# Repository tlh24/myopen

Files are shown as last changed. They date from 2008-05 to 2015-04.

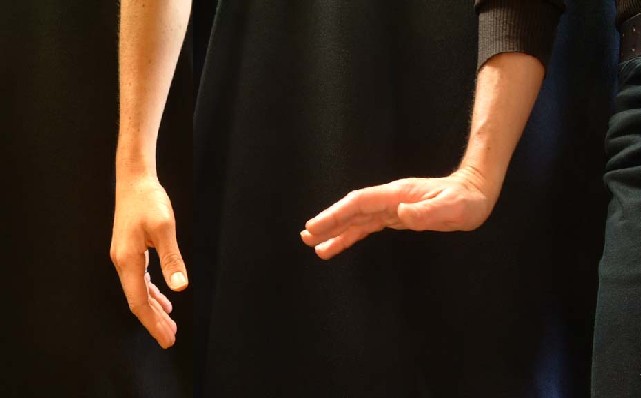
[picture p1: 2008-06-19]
MiniVIE/+PatternRecognition/Images/wrist extension.jpg

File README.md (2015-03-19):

# myopen
The Myopen project has expanded in include a number of separate modules: EMG hardware 9wired and wireless), EMG software, wireless neural recording hardware, wireless control software, and wired neural recording software.  Everything is released under GPL v3. Below is the old introduction. 

----

OPP is seeking to encourage experimentation with myoelectric control in order to inspire more rapid development of mechatronic prostheses for amputees. Because of the extremely small market size for upper extremity prosthetics, we think that one way to encourage this activity is to develop toys or user customizable devices that are capable of myoelectric signal processing. With wider access and experimentation with the technology, perhaps we could see interesting developments beyond the traditional venues of corporate R&D and educational institution research.

Along with a couple of collaborators (and we'd love to have more), we are exploring the development of an extremely flexible open hardware module that could be used with the Buglabs device, the LEGO NXT platform, and as a USB device that could be used with the OLPC (laptop.org), and traditional linux and windows computers. The components of the device would be modular, so we could populate them as needed, and use the same design for a variety of applications. The USB interface could also be used for connecting to game consoles, such as the Xbox360 and Playstation 3; the I2C bus may be useful for connecting to the Nintendo Wii via the Nunchuck input.

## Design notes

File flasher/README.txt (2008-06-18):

You need to have libparapin installed to make this work. 
http://parapin.sourceforge.net/
connections for making a cable: see flash.c
note: need a 33pf capacitor between clock signal and ground 
close to flash ram for proper timing.

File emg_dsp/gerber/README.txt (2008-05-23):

Project: emg_dsp, http://code.google.com/p/myopen/

Layer Stack: 
1 - Component, Cmp, top of board.  	emg_dsp-Cmp.pho
2 - L2, inner layer, ground. 					emg_dsp-L2.pho
3 - L3, inner layer, power/routing. 		""
4 - L4, inner layer, power/routing. 		""
5 - L5, inner layer, power. 					""
6 - Copper, Cop, bottom of board.   	emg_dsp-Cop.pho

Note: all layers are viewed from the TOP of the board. See layer texts on the right of the board
outside board outline. 

* PCB to be finished to 0.065" +- 0.005" thickness, unless otherwise required.  
* PCB to be constructed of FR4, high temperature option not required. 
* Rectangular routing outline in emg_dsp-Drawings.pho
* Minimum trace/space 0.005" 
* Minimim via drill 0.006"
* Drill file: emg_dsp.drl, summary in emg_dsp-drl.pdf
* Surface finish to be solder mask over bare copper (SMBOC), green, (in *Mask_ files), both sides. 
	with 150 micro inches Nickel (Ni)
	followed by 3-8 micro inches immersion gold. 
* Silkcreen (*SilkS_ files) to be white or yellow, both sides.
* Tear dropping alowed where permissible. 
* PCB to be manufactured in accordance with IPC-6011 and IPC-6012 class 2. 

Timothy Hanson
sideskate@gmail.com
919-475-4340 (cell)
919-668-1235 (office)

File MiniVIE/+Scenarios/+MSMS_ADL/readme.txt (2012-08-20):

% 6/18/2012

PPT files are located at: 
C:\MSMS\Sample Models\WRAMC_Model\Data\ADL

From XML files, .asf and .msm files are generated in:
C:\MSMS\Sample Models\WRAMC_Model\Data

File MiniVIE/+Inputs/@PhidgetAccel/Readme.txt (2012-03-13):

Matlab with Phidgets
April 18, 2008

Matlab gets access to the Phidgets via the Phidget21 C library.

In Matlab, we use .m files as 'code' files to hold the script to access a phidget.

To set things up all you need to do is change the working directory of Matlab to
wherever the examples are and then run the example by typing the filename in the
command window.

So servo.m which moves a servo is run by typing 'servo'

The code editor opens automatically when you double click a .m file 

Details about coding for matlab:

To open a system library: 

	loadlibrary phidget21 phidget21Matlab.h;

where phidget21Matlab.h is the header file located in the local directory and plib is a
handle to refer to the library from now on.

Note that phidget21Matlab.h is not the same as phidget21.h and has special modifications to
work properly with Matlab.

here we create a generic pointer which functions as a CPhidgetServoHandle 
(which is just a typedef of long anyways) and then use calllib to call the create function
from the library for initializing the ptr:

	ptr = libpointer('int32Ptr',0);
	open = calllib('plib', 'CPhidgetServo_create', ptr);

This gets the handle from the Phidget ptr, which we need for basically all function
ie: the handle is what the ptr points to:

	handle = get(ptr, 'Value');

We then need to open the servo motor and wait until it's status indicated an attach.

Here we use the handle and also an int32 pointer to call getSerialNumber, since
we need to pass a pointer to int for the serial number:

    serial = libpointer('int32Ptr',0);
    calllib('plib', 'CPhidget_getSerialNumber', handle, serial);

We also use a timer to time the setmotorposition's but that's a matlab thing, not really important.

Note that there is no concept of funtion pointers in matlab, so we can't use events at all.
This means that we have to poll for the data. This also means that we can't use the attach event.
Since we have to use some sort of method to wait for attachment, we can use the CPhidget_waitForAttachment
method to wait for the attachment. This method takes in a handle and a timeout, with a time of 0 meaning
infinite and it won't return until the phidget is attached or the timeout expires, so you need to check
the return value - see the examples for this.

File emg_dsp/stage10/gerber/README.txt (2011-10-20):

Project: stage10, http://code.google.com/p/myopen/

Layer Stack: 
1 - Front, top of board.  				stage10-Front.gtl
2 - L1, inner layer, ground. 			stage10-Inner2.gbr
3 - L2, inner layer, power/routing. 		stage10-Inner3.gbr
4 - L3, inner layer, power/routing. 		stage10-Inner4.gbr
5 - L4, inner layer, ground. 			stage10-Inner5.gbr
6 - Back, bottom of board.   			stage10-Back.gbl

Note: all layers are viewed from the TOP of the board. 

* PCB to be finished to 0.063" +-0.006" thickness (1.6mm) 
* PCB to be manufactured in accordance with IPC-6011 and IPC-6012 class 2. 
* PCB to be constructed of FR4, high temperature option required, Tg >= 170C
* Routing outline in stage10-Drawings.gbr
	Board external dimensions: 3.05"(y) by 4.35"(x) exactly. 
* Minimum trace/space 0.005" / 0.005"
* Minimim via drill 0.008"
* Drill file: stage10.drl
* All holes to be plated through.
* Surface finish to be solder mask over bare copper (SMBOC), blue, 
	in stage10-Mask_Front.gts and stage10-Mask_Back.gbs, both sides. 
	with 150 micro inches Nickel (Ni)
	followed by immersion gold. 
* Solder mask may be enlarged as needed. 
* Silkcreen in stage10-SilkS_Front.gto , stage10-SilkS_Back.gbo  
	to be white, both sides of board.

Timothy Hanson
sideskate@gmail.com
919-475-4340 (cell)
919-668-1235 (office)

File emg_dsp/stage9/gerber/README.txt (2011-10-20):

Project: stage9, http://code.google.com/p/myopen/

Layer Stack: 
1 - Front, top of board.  				stage9-Front.gtl
2 - L1, inner layer, ground. 			stage9-Inner2.gbr
3 - L2, inner layer, power/routing. 		stage9-Inner3.gbr
4 - L3, inner layer, power/routing. 		stage9-Inner4.gbr
5 - L4, inner layer, ground. 			stage9-Inner5.gbr
6 - Back, bottom of board.   			stage9-Back.gbl

Note: all layers are viewed from the TOP of the board. 

* PCB to be finished to 0.027" +0.005" -0.002" thickness (0.68mm) 
* PCB to be manufactured in accordance with IPC-6011 and IPC-6012 class 2. 
* PCB to be constructed of FR4, high temperature option required, Tg >= 170C
* Routing outline in stage9-Drawings.gbr
	Board external dimensions: 2.4"(y) by 1.9"(x) exactly. 
	Some silkscreen will be cut off board; this is OK. 
	Tight copper/routing clearance at bottom is per design. 
* Minimum trace/space 0.005" / 0.005"
* Minimim via drill 0.006"
* Drill file: stage9.drl
* All holes to be plated through.
* Surface finish to be solder mask over bare copper (SMBOC), blue, 
	in stage9-Mask_Front.gts and stage9-Mask_Back.gbs, both sides. 
	with 150 micro inches Nickel (Ni)
	followed by immersion gold. 
* Solder mask may be enlarged as needed. 
* Silkcreen in stage9-SilkS_Front.gto , stage9-SilkS_Back.gbo  
	to be white, both sides of board.

Timothy Hanson
sideskate@gmail.com
919-475-4340 (cell)
919-668-1235 (office)

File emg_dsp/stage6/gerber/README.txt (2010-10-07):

Project: stage6, http://code.google.com/p/myopen/

Layer Stack: 
1 - Front, top of board.  				stage6-Front.gtl
2 - L1, inner layer, ground. 			stage6-Inner2.gbr
3 - L2, inner layer, power/routing. 		stage6-Inner3.gbr
4 - L3, inner layer, power/routing. 		stage6-Inner4.gbr
5 - L4, inner layer, ground. 			stage6-Inner5.gbr
6 - Back, bottom of board.   			stage6-Back.gbl

Note: all layers are viewed from the TOP of the board. 

* PCB to be finished to 0.063" +- 0.006" thickness (1.6mm) 
* PCB to be manufactured in accordance with IPC-6011 and IPC-6012 class 2. 
* PCB to be constructed of FR4, high temperature option required, Tg >= 170C
* Routing outline in stage6-Drawings.gbr
* Minimum trace/space 0.005" / 0.005"
* Minimim via drill 0.006"
* Drill file: stage6.drl
* All holes to be plated through.
* Surface finish to be solder mask over bare copper (SMBOC), blue, 
	in stage6-Mask_Front.gts and stage6-Mask_Back.gbs, both sides. 
	with 150 micro inches Nickel (Ni)
	followed by immersion gold. 
* Solder mask may be enlarged as needed. 
* Silkcreen in stage6-SilkS_Front.gto , stage6-SilkS_Back.gbo  
	to be white, both sides of board.

Timothy Hanson
sideskate@gmail.com
919-475-4340 (cell)
919-668-1235 (office)

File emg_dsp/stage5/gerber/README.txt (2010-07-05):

Project: stage5, http://code.google.com/p/myopen/

Layer Stack: 
1 - Front, top of board.  				stage5-Front.gtl
2 - L1, inner layer, ground. 			stage5-Inner2.gbr
3 - L2, inner layer, power/routing. 		stage5-Inner3.gbr
4 - L3, inner layer, power/routing. 		stage5-Inner4.gbr
5 - L4, inner layer, ground. 			stage5-Inner5.gbr
6 - Back, bottom of board.   			stage5-Back.gbl

Note: all layers are viewed from the TOP of the board. 

* PCB to be finished to 0.047" +- 0.006" thickness (1.2mm) 
* PCB to be manufactured in accordance with IPC-6011 and IPC-6012 class 2. 
* PCB to be constructed of FR4, high temperature option required, Tg >= 170C
* Routing outline in stage5-Drawings.gbr
* Minimum trace/space 0.005" / 0.0045"
* Minimim via drill 0.008"
* Drill file: stage5.drl
* All holes to be plated through.
* Surface finish to be solder mask over bare copper (SMBOC), blue, 
	in stage5-Mask_Front.gts and stage5-Mask_Back.gbs, both sides. 
	with 150 micro inches Nickel (Ni)
	followed by immersion gold. 
* Solder mask may be enlarged as needed. 
* Silkcreen (stage5-SilkS_Front.gto , stage5-SilkS_Back.gbo ) to be white or yellow, only top of board

Timothy Hanson
sideskate@gmail.com
919-475-4340 (cell)
919-668-1235 (office)

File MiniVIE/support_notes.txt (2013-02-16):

Support Notes
--------------

Tested with Matlab 2010b on WindowsXPSP3 32-bit
Tested with Matlab 2010b+ on Windows7 64-bit (all execpt DAQ toolbox)

Requirements: 

For use of the DiscriminantAnalysis SignalAnalysis Classifier modules
Statistics Toolbox

For use of the DaqHwDevice input object
Data Acquisition Toolbox.  See http://www.mathworks.com/products/daq/requirements.html

Data acquisition toolbox notes:
* For external DAQ devices, these typically require third party driver software.  

* Measurement Computing products need the InstaCal driver software installed.  
  Channel modes (e.g. differential versus single ended) should be configured with that tool

* National Instruments board require the nidaqMX driver suite, available from the NI website
  The complete install package is ~1.5GB, however you can alternatively download and install
  the nidaqmx_core library which is only ~150 MB

* Important: Please follow the instructions for registering the install DAQ device with the 
  MATLAB environment.  This typically takes the form:
  >> daqregister('nidaq')  % RUN AFTER LAUNCHING MATLAB IN ADMINISTRATOR MODE

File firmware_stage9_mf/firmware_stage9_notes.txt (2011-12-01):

December 1 2011
	Thoughts: really should put the LMS *after* filtering -- it just serves to 
	get rid of the 60Hz, which the filters can deal with effectively already. 
	If it's after the IIR fitlers, it will 'concentrate' more on in-band common-mode
	noise.

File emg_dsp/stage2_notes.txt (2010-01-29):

stage2 notes: 
x array distance on the LMV1023 circuit: 0.247"
y array distance : 0.057

Feb 11 2009: changed input capacitors from 1uf to 0.47uf to have 
better rejection of ECG; updating the digikey order accordingly. 

March 10 2009 - 
NEED THERMAL RELIEF around all through holes; otherwise, cannot solder them! 
(at least, not with a soldering iron; may be able to reflow them)
NEED more space around the electrolytic cap -- or need a surface mount cap. 
	 I'm just going to leave it out for now. 
NEED to get the large-bumped package for electret amps: LMV1032UR
FOOTPRINT for SOD-523 and SOD-323 are incorrect; need to use SOD-523 for both 
	on board (3.3 and 5v zener protection).  
	http://www.diodes.com/zetex/_pdfs/3.0/pack/SOD523.pdf
	http://www.diodes.com/zetex/_pdfs/3.0/pack/SOD323.pdf
	323 is BIGGER than 523 (wha?)
FOOTPRINT of nRF24L01 too small - fixed. 
	the top pads were off by 0.25mm !  (1.5mm instead of 1.75mm - 
	changed to 1.85mm for better exposed die clearance)
FOOTPRINT of LFCSP-48 enhanced.  should be OK now, though - just no overhang. 
	set overhang to 0.2mm. 
VOLTAGE of the MAX3421E is 3.3V - it does not run at 2.85V!! DOH! 
	next time need a 3.3v LDO off the USB power for this chip!

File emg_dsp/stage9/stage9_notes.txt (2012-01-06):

Fixes to stage9: 
* Need to have a hole or somethingunder the 9-pin omnetics conmnectors: 
	connectros shear off easily
	Alternately, need a different connector system. 
* Bipolar transitor on the input to prevnt breaking in the case the battery polarity is wrong
* Lower voltage (0.85v) , lower clock rate w/ simpler firmware
* Use cuts not jumpers for the ground / reference configuration. 
** Slight ground currents should not matter, I hope. Need to think about this. 
* Realy should use the impedance measurement -- should be a very useful feature. 
* Also, an accelerometer or some other way of measuring state ... will have to transmit that
** can multiplex on one continuous channel.
* LFP would be nice too. Expand the analog filtering? 
* Might be nice to use something else to derive the MUX signals, and do block computation? 
	Have to think about this .. issue is that we are wasting clocks sometimes waiting for samples.
	Really need a much lower-power processor. 
* Add 2-4 channels microstim(?).  Must be careful about ground-loop: use a separate proc. 
	or a separate battery; have to think about this.

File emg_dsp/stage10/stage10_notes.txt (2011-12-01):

fixes to stage10: 
 * need to connect R118 to ground. This is the APD signal on the PoE chip.
 	(not absolutely needed for device function, but should be fixed.)
 * regulated output of PoE converter is 2.5v -- off by a factor of 2? 
 * Anode and cathode are reversed on the TLE431 (!)
 * Really need to have a switch on the PoE input -- so we can turn off the switching there.

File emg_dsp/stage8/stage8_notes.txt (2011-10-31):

Notes from debugging stage8
February 25 2011
* Most everything works properly on the board -- no hardware errors yet.
* Digikey shipped some incorrect resistors, which is annoying - they 
	have not done this before, to the best of my knowlege - 
	but a relatively easy fix. 
* The new solder paste - ZeroLead no-clean solder paste - 
	http://www.ameritronics.com
	works well, better than previous.  Unfortunately they don't ship with caps. 
* Issue: headstage seems to be transmitting data well (at least looking
	at the control signals).  RX fails about 50% of the time.
	only thing that has changed is the incoming data rate. 
	Hence, let's try writing data more slowly - at original rate.
		same issue.
		probably is something in the radio code.. 
	Perhaps it's a framing isue: SPI clock too slow, some bits get cut off?
		changed rate to 13.3Mhz - no change. 
		Strangely, we seem to get IRQs in the middle of where they should be.
		Notable is we've changed the cycle time from 2us to 1us
		natrually there will be issues.
		Added some extra pipeline stalls, nothing..
		Perhaps should try slowing down the sample clock for the same effect?
		Halved the sample rate -- did not fix problem. 
		Still unreliable packet transmission.
		Must be the radio control code.
		Try the C-version: seems broken! JTAG time.
	C version working.  SPI clock running at 10Mhz, as per asm version.
		primary difference seems to be that the packets are uploaded in bursts, 
		not continuously like the other. try change.
		continuous packet uploading does not break C version for radio controller.
		Let's compare..
		seems there's an extra clearfifo bizness... check if that makes it work.
		radio_clearfifos makes the return packet arrive more reliably, yes.
	Think the radio control routine is the same as the C version -- 
		have not checked with JTAG yet -- 
		but still does not work :-(
		aggregate data rate appears to be about the same
		data bus appears to be active at the right times..
		where are the extra / skewed packets coming from? 
		is this a data content issue? 
February 28 2011
		YES
		changing the data to 0xa5 for all samples fixed the error!  yay!
	Proc seems to be waiting too long for the RX packet. 
		usually the bridge can respond within 360us
		presently we're waiting 780us
		current serial RFS is 29 / was 19 -> equivalent wait of 511us
		Should wait 180 samples; 190 ought to be enough.
			(there are two calls to _get_asm in the loop of waitirq)
	Perhaps I've overestimated the outgoing bandwidth. 
		It takes 1.36ms to transmit 256 bytes (measured)
		It takes 360us for the bridge to turn around and get a response.
		Total is 1.72ms. 
		Frame time, with 7 samples per packet, 56 samples per frame is 1.792ms
		much too close, apparently! 
		setting waitirq to 172 allows the 'stage to work.. not exactly sure why though.
		anything below 160 misses out on TX sent IRQs.
	Really need to fix the data bug - simplest, and best, way is to add AGC. 
		working on AGC: IS (integer signed) mode is
		ESSENTIAL
		when transferring accumulator to register.
March 1 2011
	Got AGC working properly.. finally. 
		Turned out that i hadn't though of the magnitude of the components properly.
	Next, most important issue: make radio transmission reliable. 
		If we transmit 0xa5 for all bytes, all packets seem to get through.
		If we transmit 0xcc, same.
		0xc0, same.
		0x80, same.
		0x00?  same!!
		0xff?  fail!! aha.  I guess.
		0xfe? works..?
		0x01, works.
		XOR data with 0xa5 fails.
		AND data with 0x7f fails.
		AND data with 0xbf fails.
		AND data with 0xdf fails.
		AND data with 0xef fails.
		AND data with 0xf7 fails.
		AND data with 0xfb works.
		AND data with 0xfd works.
		AND data with 0xfe works.
		
		Slowing down the SPORT to half the speed - hence giving more time between 
		SPI transfers - does not fix the issue.
		whattt is it? perhaps contention - something else (nordic?)
		is trying to drive bus?
		Doesn't look that way - the busses are separate. 
		Which byte is it?  can possibly send 0xaa as the first byte, technically only need
		31 bytes payload.
March 2 2011
	(Continuing above)
		Tried sending 0xa8 as the first byte .. reception is still noisy. 
		What if we change the radio channel? 
		Why did this error not appear before?  Is it hardware-dependent?
	trying stage5. 
		it RXes every other packet,  more or less.
		but program does not fit hardware well... hmm.
	trying different radio channel (0) -- no change. 
		same issue. dropped packets. 
	trying to AND data with 0xfe - 8 bit TX to 7 bit - make difference?
		yea.  that works.  WHYYYY?
	Ok, I understand why - the bridge is getting confused by the new packet setup, 
		and is spontanteously going into RX mode during a frame, thereby missing 
		vital packets. 
		What we need to do is re-write the bridge code to accomidate the higher b/w
		and possibly to extend the frame to 16 packets. 
	Trying the processor at 400Mhz -
		looks like the MAD does not work, or does not complete in time, at this frequency. 
		really should increase the core voltage. 
		At a core voltage of 1.0v (was 0.85v), the processor seems to run normally. 
		current is 100ma. (about)
		Stops working just at 0.85v.
		That said, looks like @ 400Mhz we have plenty of time for adaptive noise
		cancellation, if it's decided that will help! 
		(at what place in the pathway should we do this - befroe AGC I guess?)
April 8 2011
	Current consumption: 
	60mA, 4.12v, everything enabled, one LED on 5ma 2.85v -> 3.5ma@ src
		should be 56.5ma w/o LED. 
	47.5ma, 4.10v, two headstages connected, one LED -> 44.0ma @ src
	41.8ma, 4.10v, one headstage connected, one LED -> 38.3ma @ src. 
	----
	each headstage consumes about 6ma from the source. 
	The intans are listed at about 4.1ma each (supplied directly from bat, not switched)
	The ADC is listed at 2mw -> 0.75mA, also supplied from the bat, 
	so we have about 1.2ma unaccounted for --
	probably attributable to computation? 
	or the intans use more current than expected?
	Well, anyway. let's say 60ma, want the thing to run for 24 hours. 
	That's 1440maH.  can get that in a cell phone battery .. easy. yay! 
	do i want to record more than 128 channels? nah. 
	----
	Other things to do: 
	* audio out working on base station. constant rate sample consumption? 
	 variable rate? hm. (fixed)
	* decorrelator in the spare cycles?  (done)
	* fractional gain (done)
	* flat response has inappropraite gain?  (fixed)
	* sample different parts of the signal chain. (done)
	* longer waveform drawing -- should go to the end of the screen in zoom = 0.2
		(done)
	* be able to turn AGC off. 
	* fix the draw bug on neuro-nico. seems to be pre-GPU, since if you switch 
		the indicies of the VBOs, the yellow is then drawn correctly.
		methinks its a 64-bit issue. which is indeed an issue.
	----
April 9 2011
	Tested radio + triple diversity RX -> works very well. 
	Can position the transmitter by the window & not have too too many dropped packets.
	add another filter option? 
April 14 2011
	Implemented 3 versions of LMS: 
	* simple, direct 7 tap filter, error computed via shift >>>
	* pseudo-LMS style, error saturated to +- 1, signal saturated to +- 1
	* summing pseudo-LMS style, sum 3 samples, 4 weights, sum saturated to +- 1, 
		error saturated to +- 1.
April 18 2011
	* Noted that audio output seems to contain pops and clicks; worried that 
	this may be a result of 
	(1) processor operating at a too high clock rate -> errors in math
	(2) errors in transmit pipeline due to stalls. 
	To test
	(1) clocked proc slower. 288Mhz, 720kHz ADC. 
		No change in pops as recorded to disc.  
		the pops seem poisson - most likely the radio is at fault!
		Can we detect these as false spikes? 
	(2) clocked ADC slower. 800Khz -> more cycles to service radio.
		No change in pops as recorded to disc.
	Looking at the data, it is clear that sometimes the packets are *not*
	being sent out on the wire in order - some packets are dropped, but 
	the ones put in their place are not always those dropped. 
	It almost looks like they were hanging around from some old buffer. 
	And this appears poisson ..? Network noise?
	Must be a bug in the stage7 firmware.
	Observations: 
	* Never messes up channel assignment - when channels have two different
		sine wave amplitudes, the pops never exceed that amplitude.
	* Errors are concomitant, generally - the occurr on a per-packet basis
		The only time you only hear on one channel is when the error is less audible 
		on the other channel.
	* Error is alwas preceded by a dropped packet - less noticeable - and an 
		addition of an unkown packet. 
		Is this packet a reminant of an old transmission? 
		Will have to erase after write-out to see! 
	YES, if we clear the buffer to 0, all unkown packets are 0 packets. 
		must be that 'gotx' or 'go tx' is being triggered before the buffer is
		completely full (recall frame = 16 packets; UDP_PACKET_SIZE = 512 = 32*16)
		This implies that packets are being dropped, which is not surprising, 
		even though the radios are right next to eachother..?
		What about antenna diversity? Could be that another antenna RXed the packet.
		Really need to analyze antenna diversity & how the SW degrades. 
		The only reason I have packet transmission tied to RX packet is that 
		this seems like a good pause for servicing eth..
	okay. now the packets are properly dropped rather than having bogus data inserted. 
	Next: check antenna diversity.
		Antenna diversity is working!  any of the three antennas is capable of picking
		up signal. However, three together do not seem to reduce the error rate to zero. 
		perhaps it is exogenous noise? 
		or ethernet interupts? 
		Kinda hard to test the eth theory -- we need to listen to packets!
		Try disabling the audio out? 
			No difference.
			Maybe I should just sleep on it.
	Ok, try to fix the audio out, which is emmiting wobbly shit.
		putting it in only normal mode. lots of staticky noise, probably from having 
		only 16-bit samples. 
		bah, need an antialiasing filter here.
April 19 2011
	Testing headstage current: 
	(everything running, full LMS 320Mhz / 80Mhz / 1Mhz ADC)
	3.11V	75.1ma  (minimum voltage - below this signal is distorted - probably LDO drop-out)
	3.20	73.2
	3.30	71.6
	3.41	69.4
	3.56	67.3
	3.71	65.9
	3.83	64.6
	3.96	63.1
	4.07	62.0
	4.23	60.6
	4.38	59.3
	4.49	58.5
	4.57	57.9
	4.77	56.6
	5.04	55.0
	5.21	54.1
	5.34	53.5
	5.64	52.0
	5.80	50.9
	6.05	49.8
	6.19	49.2
	6.35	48.7
	Linear fit gives: static power consumption 153 mw (with LED!), 24.6mW/V slope
	(so about 25ma static draw, 50ma dynamic @ 3V)
	check: 4V / 150mw = 38.25 dynamic + 25 static = 62.85Ma; actual = 62.15.
	Capacity required with a mean Li-ion voltage of 3.56V - 24*67.3 = 1615maH
	probably want at least 2000maH, or better. 
	could reduce code complexity to reduce power .. but I hope all this stuff is useful.
May 25 2011
	Added template sorting to both headstage and client -- whew. 
	Have to clock the processor at 0.95V, 400Mhz now; 
		let's check the power consumpion.
	3.31	84.2ma	278mw
	3.50	80.5	281
	3.70	77.9	288.23
	Assuming average current consumption of 80ma (note - with LED), 
	one RediLast 2900 battery should power one headstage for 36 hours. 
		(if not more - see 
		http://lygte-info.dk/info/Batteries18650-2011%20UK.html 
		which shows 10.5Wh -> 37hours @ 282mw)
October 26 2011
	Jesus!  Where did the time go? 
	Still confused about the "headstage says match, we don't find" error. 
	Is it bit-error noise? 
	Have to make sure the aperture & template are being updated properly;
		I have a suspicion that the GUI is not always being updated, esp. after sorting (?)
		Seems to update after sorting, yes. 
	Ok, juice!

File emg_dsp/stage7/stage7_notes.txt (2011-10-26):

Hardware fixes: 
	* Need filtering on the testcon _CS signal too! 47pf fixes issue. 
	* MIC5365-2.5 supplying Votp for blackfin is not attached to Vdd. 
		fixed in schematic.
	* Labels on LEDs are incorrect. 
	** Be very careful about LED orientation in robot! 
	* Capacitors on audio out are mounted too close to the 1/8" jack body.
		can fix with sensible placement prior reflow.
		
Software: 
	March 25 2011 -- 
	one radio seems to work well; interaction of all 3 radios, 
		however, does not work. Looks like radio 0 tmies out at some point,
		holding it's CSN line low. 
		what would be doing this? 
		(as an aside, reverse directon seems not to work - 
			cannot modify headstage channel)
		trying to enable 2 radios.
		Ok, with two radios, looks like radio1 is not always after radio0,
			and that twice as much data is coming out of the bridge.
			(the 2 channel scope is a real liability here). 
			(I really need to get my logic analyzer)
	got three radios working .. seemingly. 
		getting about 10530 packets/second in the client. 
		for 128 channels, measured frame rate is 279.3 frames/sec, 
		which equates to 4468 packets/second.  Observed rate is 2.35 times larger - 
		clearly I need a better means of radio state control. 
		I think what's going on is that the program is desynchronized with 
		incoming radio packets: we are setting 'write' to 1 when
		one radio still has a packet in the fifo.  
		Therefore only set write to one when all radios are serviced? 
		woohoo looks like antenna diversity is working! yay.
		now need to check on the thresholding. 
	thresholding: why no work? 
		deal: need to test with *actual* signals, not just noise.
		behavior: changing the channel works. 
		setting the threshold makes the threshold crossings more realistic. 
			changing the threshold seems to not change threshold crossing density.
		changing the channel subsequently reverts threshold channel display.
		aright, that's fixed - pointer wrap issue.
		now the problem is that the display is fruitcaked. as in, caked in fruit.
		spikes are not aligned with threshold crossings. 
		breaking down the issue further, fixed the channel ordering problem; 
		now it seems that the order of thresold crossings in the spike display 
		is inverted per 32 channels. 
		that would be because that's the way it is in the schematic! 
	need to test by setting channels to oscillate (sinusoid)

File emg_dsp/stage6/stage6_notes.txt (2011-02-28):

Hardware Fixes: 
	* The LEDs are TOO bright!  decrease the current to a more reasonable 
	level.  Current LEDs Vf = 2.0V :: 26mA of current. 10ma better -> 
	need 130 ohm resistors.
	Total power dissipation of 16 LEDs: 1.3W..?
	* Vdd_OTP NEEDS to be tied to 2.5V for the proc to boot.
	I guess I'll need a regulator here.
	(I assume this is needed by the security code)
	* Need caps on nordic lines to quench ringing (47pf, SCK & MOSI)
	* R61 & friends were not grounded (on the schematic) oops!
		Can jumper to R12.
	* The labels on the external power supply are SWAPPED! 
		28 is 0.8V, 08 is 2.8V! (or more accurately, 2.65V, as measured)
	* On EMG section, input to OR gate must be RSCLK0, not TSCLK0. 
		TSCLK0 is only used to generate TFS0.
		Both clocks are output. 
	* switching regulator needs to be further away from EMG input section.

November 8 2010
	* Wrote a simplified .dxe - one that just toggles a few pins - 
	and the BF527 seems to run. Next: see if we can get the SPI interface running. 
	(this will show if the SPI pins are connected - the proc does not boot, 
	but this is likely because the flash originally ordered was a 2V part)
	* putting the SDRAM in self refresh works. 
	* setting the core clock at 600Mhz and the system clock at 125Mhz 
	seems to work as well. the toggle rate is 6.666Mhz now; was 1.5Mhz.
	(I'm sure glad JTAG works!!!)
	* looks like the SPI port is working! Not sure why it doesn't try to boot..
	* Next task: get the UART working. soo useful. done.
	* SDRAM: initalized.  works, checked!  yay!
	* Ethernet: need to have a milisecond counter running first, in an interrupt.
	* Ethernet: works.  DCHP and all!
November 9 2010
	* Next: get the radio working. Needs to be soldered there first! 
November 12 2010
	* okay, the bridge - at least in a debug build - seems to work. 
	The radio is very sensitive to timing / sequencing: notably, NRF_CE
	must be low while uploading the response (command) packet.  
	so be it.  
	* -O3 does not work, for whatever reason.  ??  just use -O or -O2.
	* if you put the headstage in oscillate mode, it still appears that there
	 are dropped packets. perhaps it is the client..?
	 the trace from UDP packets indicates that nothing is being dropped, 
	 and the o-scope similarly looks good. 
November 15 2010
	* I guess the next thing is to try out the new version of the headstage..
	does not seem to transmit packets reliably. electrical issue?
	tried hand-soldering all the pins again - from the outside, without removing
	the chip, and no difference. 
	perhaps in the future I should have protronics put both the RHA2116 and 
	nRF24L01+ on the board?  Seems I'm not too good at it .. :-/
November 16 2010
	* Tried the same fimware with the first build of the headstage on stage6. 
	Looks like exactly the same behavior... therefore, it's probably not 
	a hardware issue (if it were, then the two different builds would 
	probably have different behavior). 
	Is it possible that the problem is bad data? e.g. sending 0x0000 for all
	samples leads to corrupted packets? 
	Perhaps one of the RF components is bad / the incorrect value? 
		This would affect output power, presumably, and for the small distances
		that i'm testing the radio at, there is no difference wrt orientation. 
		If the power were iffy, then changing orientation would affect response.
	Seems unlikely to be the SPI bus - both BF532s boot properly (so far as I can tell)
	Power supply voltage?
		Changing the supply voltage to 2.5V from 3.3V changes nothing. 
		(below 2.5, the processor is in reset, properly so)
		It's unlikely that changing the core voltage from 1.2 to 0.8 will change
		anything but the proc power dissipation.  The BF532 is rated at that voltage.
	Note the old version of the headstage - stage5 - works reliably. 
	* I guess the appropriate thing to do now is to mess around with software, 
	see if we can delve into why it's unreliable. 
	Okay! radio_tst_bidi() transmits 8 packets reliably, but does not RX the resulting
	command packet.  Hence, it is a software thing .. let's see if transition to RX 
	is there ..?
	Is putting the radio in off mode (NOR_CONFIG 0) needed? 
		No. (prior RX mode .. but then again, it doesn't rx the packet.)
		No. (prior TX mode). 
	radio_tst_bidi() does not work on stage5!! IRQ is never asserted.
Novemeber 19 2010
	present version of neurorecord (262) works when compiled with -O
	and uploaded using JTAG to headstage. 
	serial port is somehow borked, which sucks -- speaking of which should
	have ran some lines out so we can get the headstage serial on the bridge
	port -- but not a serious issue. 
	present version of the code flashed to stage6 headstage works fine, actually
	**provided** that the USB endpoint is not connected. 
	The instant you enable the USB endpoint, reception of the status packet
	falters.  
	Looks like it only sends full status packets when it says so...
		and it does not seem to be claiming so.
	Even after you disable the USB endpoint / kill the client, packet reception
	is still flaky: not all command packets are recieved. (as indicated by the IRQ line)
	Restarting the radio resets this behavior to default-good. 
		(without resetting the bridge, which implies that it's the firmware on 
		the stage6 headstage)
	perhaps flush the fifos when switching states? 
	if you try to debug the headstage without a hardware reset, it fails. .. why?
	flushing the fifos when switching states does fix the behavior. 
	rather, it appears that every other RX packet is dropped, and the proc
	simply waits forever for it..
	turning on and off the pc-side client does not affect this behavior. 
	perhaps its a synchronization issue?  
		No, as its a flag that tells the bridge to send a command packet.
	** okay, with the mode switching, looks like all packets
	get through ... with high reliability. perhaps the problem is the flag is
	not being set.. ? 
	it doesn't look like the bridge is even trying to send a command packet.
	doesn't look like the packet format changed..
	ugh, not sure bout this
	if I put in a clear-fifo command before starting the transmit-only while 
	loop, it's more reliable but not completely so: bridge only gets 7 packets
	before deciding to transmit a status pkt. 
	seems like there is a systematic offset somewhere.. ?
	now looks like the first packet is not getting through. why?
		adding a bit of delay between uploading the packets seems not to matter.
		on the other hand, USB seems super reliable now.  huh.
		clearing the fifo and re-writing the configuration also doesn't matter.
	* okay, drastically simplified the data write - one packet at a time. 
		it works fine. very consistent. 
		of course, there is no memory writing going on. 
	* let's use sample() instead of spi waits. 
		YES that works.
	* try no memory writes in real prog.
		sorta works ... IRQ not getting cleared.
		fixed, added a fifo clearing. 
		now, data transmitted does not make sense!
		It is ''definitely'' the memory read / write. perhaps to the wrong loc? 
	* putting the RX mode back in there.  
		Of course it does not work - need to send out the packet special byte. 
		Now, bridge sees the special byte - and sends out a response - 
		but the headscage does not hear it? 
	* AHA!! the bridge does not have CRC ON!!! 
		It occurs to me that CRC should be on bigtime when writing mem
		but: not the other direction!! IMPORTANT
	* turning back on memory writes. there seems to be some systematic offset.
		wtf?
	* It seems that this hardware is somehow more 'fragile' - the pointers are 
	 more likely to go out of bounds or become desynchronized. 
	 not really sure why.. 
	 	Also: have a hard time programming the flash now.  more hardware gremlins?
	* Anyway, now looks like we're not getting to RX mode fast enough.
		Or, more accurately, still desyncronized. 
November 22 2010 --
	* Finally, got stage6 headstage werkin -- as the SVN log will attest, it *WAS*
	setup / hold violations.  HAve no idea why the C version does not work reliably, 
	but the ASM version does, and that is what matters. (neurorecord svn ver 265)
	* Now: ethernet client does not switch channels properly.  hum hum. 
		does switch with USB bridge, that packet dropping ho. 
November 30 2010 - back to work after a wonderful thanksgiving holiday. 
	Everything is basically working, as expected. 
	* Issue: client needs to be told the IP address of the bridge. is this reasonable?
		Yes, I guess.  In the future there will likely be more than one headstage, 
		more than one bridge. 
	* Issue: no Intan chips on the headstage.  I guess I should install them? 
		Assuming that I can?  or gear up for producing more headstages?
		Probably best to test this wireless headstage in a mk, asap.
	* Omnetics connector FAIL.  Fell off while I was inserting the jumper to the 
		headstage test board; these must be mounted properly the first time
		(they tend to warp during reflow), then glued to the board.
	* Thresholding is not working either. check the code. seems to be off by one bit:
		Looks like seeting gain high on channel 0 yields threshold of 0x3 (0b0011)
		setting gain high on channel 1 yields threshold of 0xc (0b1100)
		channel 2, 0x30. 
		This is the same on stage5, as expected. 
		Everything seems multiplied by 2...?
		Try channel 16, 0x2 
		channel 17, 0x8
		Perhaps this is a strange consequence of how VIT_MAX works? 
		aha!  "The accumulator register must be cleared before issuing VIT_MAX"
		Indeed, it does. 
	* Issue: seems to detect both positive and negative excursions.  Is this desired?
		(otherwise, seems to be working)
Novemeber 31 2010 -
	* Should have a disable-filter mode on the headstage, too. 
		Done. Works as expected. 
	* Using the flat-filter mode, threshold is definitely bidirectional - abs. 
		Fixed.  VIT_MAX instruction only has 15 bits of dynamic range - so we simply 
		divide both samples by 2 (>>> 1 (v) instruction). 
		and divide the threshold by 2 prior transmission.
	* Next up: work on the client program: 
		+ need to save to disc and visualize spikes. (threshold crossings)
		+ need to be able to invert gain. (that should be easy)
		+ make the gui more reliable - raw x events is not cutting it! 
December 2 2010 -
	* Decided to move to gtk2.0 as a gui toolkit for the client. The simple X protocol
		was not cutting it!   Now, have to migrate...
December 13 2010 -
	* gtk2 gui mostly done, functional though there is still a segfault bug somewhere..
	* want to measure current consumption of the core, and try to optimize.
		Headstage is by default running at 240Mhz @ 1.2V (same as BF527)
		Step signal is on PF8 -- looks like max codepath is 528ns, so it is 
		almost possible to knock the clock down to 120Mhz.
		Is this long codepath dependent on RXing a packet? 
		No, with the bridge off, still get it.
		I could simplify the filtering perhaps... hm. 
	* CLI/IDLE/STI seems to take about 180ns. 
		make little sense to do this; might as well keep it in a software loop.
	* Power figures, 
		CCLK 160Mhz SCLK 80Mhz: 
		Proc runs & boots at 0.7v.
		static current at 1V about 7ma.
		0.630v ; 19.42ma ; non-operating.
		0.641v ; 28.49ma ; 18.26mw
		0.668v ; 29.70ma ; 19.83mw
		0.708v ; 31.98ma ; 22.64mw
		0.739v ; 33.56ma ; 24.80mw
		0.793v ; 36.78ma ; 29.17mw
		0.806v ; 37.42ma ; 30.12mw
		0.849v ; 40.08ma ; 34.03mw
		0.944v ; 46.24ma ; 43.65mw
		0.997v ; 49.39ma ; 49.24mw
		1.087v ; 55.41ma ; 60.23mw
		CCLK 80Mhz SCLK 40Mhz
		0.622v ; 12.20ma ; non-operating
		0.649v ; 16.17ma ; 10.49mw
		0.705v ; 18.04ma ; 12.72mw
		0.752v ; 19.60ma ; 14.74mw
		0.804v ; 21.51ma ; 17.29mw
		0.857v ; 23.51ma ; 20.16mw
		0.908v ; 25.52ma ; 23.17mw
		0.951v ; 27.28ma ; 25.94mw
	* Possible clocking schemes. 
		160Mhz (x10) - CCLK 80Mhz - cpu ultilization about 60%
			2.830V ; 8.81ma ; 24.93mw
			0.813v ; 33.66ma ; 27.36mw
			proc operating at  at the same time.
			proc stopped: 2.23ma
			total power, excl intans: 52.29mw ; 69.59mw w/
			Intans: 7mw from 3.0v supply, 17.3mw from battery
			(operating from 2.8V supply will save 4mw -- not worth it --
				only adds 3 hours to the optimized figure)
		80Mhz (x5) - CCLK 40Mhz - must disable oversampling, every read
			sample counts.  both ADCs run at 10Mhz / 500ksps.
			2.800v ; 6.65ma ; 18.7mw
			0.813v ; 21.09ma ; 17.14mw
			have the extra cycles for this, at least..
			total power, excl. intans: 35.85mw ; 53.15 w/
	* Have: cell phone battery, rated 800mAH, 3.6v -> 2880mwH
		consumed at 69.6mw, this will last 41 hours. (full x2 oversampling)
		consumed at 54.2mw, this will last 54 hours.
		of course, probably want to run multiple headstages.
		Assuming we are running 4 headstages and we want them to last 30 hours, 
		need a 6.5wh battery, or 1800mah.  This should be possible - cell batteries 
		can be had in 2200mah size.
		2200mah will run 6 headstages for a full day, about (excluding conversion efi)
December 16 2010 -- got the headstage working (apparently) properly @ 80Mhz. 
	Can save a bit of power at this rate (8mw proc, 6mw ADCs). 
	So far as I can tell, we don't need the oversampling; the fidelity is
	limited by the fidelity of the input from the electrodes. 
	The problem was clocking the SPI port too low (5Mhz); this seems to have
	cause alignment error when reading packets RXed from the bridge. 
	Also changed the bridge to reset the RX fifo when sending packets over
	ethernet. Appears to have made everything more reliable. 
	* Need to indicate when the gain is saturated.  Seem to occur relatively soonish. 
December 17 2010 -- The headstage has been separated!  It consumes:
	15.0ma @ 4.18v = 62.7mw
December 21 2010 --tested the headstage in mango, RHA2.
	It worked, but! :
	* The splitter did not work, at least not obviously.  With the headstage
		plugged directly into the short jumper, got spikes on the 
		expected channel (4)
		Nonetheless, need to verify channel correspondence. 
	* The client has a tendency to quantize waveforms: that is, it holds 
		samples so that you get flat plateus in the WF view.  
		I've never seen this on the other computer; might be 
		a hardware problem? 
		Problem resolves after turning it off & restarting it. 
	* Need to see threshold in waveform view. 
	* PCB makes it difficult to insert directly.  Need a direct edge connector, 
		with an appropriately thinner PCB. 
	* Periodic noise on many channels. 
		Tested in matlab: noise has many many harmonics at 145Hz, which 
		is exactly the frequency of the radio.  
		Hence, must be either the radio or the serial bus controlling it. 
		(Last time it was, or appeared to be, the serial bus...hmm)
	* Movement artifact still gets through, but this is unespected, since 
		there are no ground loops!  Is this through the jumper wires? 
		Some grounding / referencing issue?  hm. 
	* Need to be able to negative-side thresholding.  
		Just set a negative gain. 
	* Possibly need antenna diversity, or circularly polarized antennas. 
		In some head orientations, most packets were dropped. 
	* Recorded 3-10MB for each channel, including the best channel (4). 
		Was not able to compare against plexon in this case. 
	* Power cable is weak, need something better, more robust. 
January 7 2011 
	Looking at the noise issue - is it the radio, or is it the serial bus? 
	Tried putting a 0.1uf cap on R138 - 7.5K bandwidth setting resistor. 
	Did not seem to change much, or at least did not eliminate the problem.
		(That said, the resistor still should be further away from SCK!)
	Channel 17, in particular, seems quite bad. 
	apparent channel mapping: (tester -> headstage 001)
	1	0
	2	off
	3	14
	4	off
	5	12
	6	11
	7	10
	8	9
	9	8
	10	7
	11	6
	12	5
	13	4
	14	3
	15	2
	16	1
	17	off
	18	18
	19	19
	... all between work.
	31	31
	32	16
	* When I stuck a small antenna into Ch 27 on the tester board, the noise did
		not appreciably increase, even if the antenna was pushed close to the 
		TX antenna.  Hmm. Add this to the fact that ch17 - open circuit - is the 
		worst, and I wonder if it's RF or something else. 
		Short out input stage, and some of the normal noise goes away.
		Perhaps the ADC is being influenced by the radio or serial bus? 
	* Tested with Misha the wireless headstage next to the wired headstage
		(plugged into the rest of plexon, of course)
		it **does** induce frame-frequency (137Hz) noise!
			but only if i am holding it.  
		If I plug it into a neighboring omnetics, there is a lot of induced 
		noise -- yet, when I release the wireless headstage, this too disappears. 
		During this time I'm not grounded; hence must be acting as an antenna. 
		Perhaps there is coupling through the ground planes? 
	* If i were to do 64 ch / headstage, seperated -- need the following signals
		GND, VEE, Vdd, reset, step, FS, CLK, Data[0..3]
		so, 7 signals common, 2 data per 32 channels. edge flexi connectors? 
		might be able to run the intan from 2.7V.. ? hm. probably not worth it. 
		cannot run more - the blackfin has only 2 SPORTS, supporting 4 ADCs. 
		If i use a BF-538, can do 128 channels. 
January 10 2011
	* (Continuing the thought above) -- a better paln is to have one blackfin + 
		radio, BF532 known and loved, intan RHA2132, 1 ADC per 32 channels, 4 sports. 
		Then need 8 wires per digitizing headstage, so can have 2 grounds with 9-pin
		omnetics. put them on either side - good. 
	* This would necessitate a different packet pattern - just threshold crossing
		would consume 128 bits = 16 bytes, or half the packet. 
		Currently running 32 channels at 31ksps works fine with a clock of 80Mhz; 
		presumably would need 3-4x the power to process 128 channels. 
		possibly more, if we need to check more condition registers; the asm 
		will be more complicated. ugh, more debugging.
		presumably would want to stream more than one channel then; more comparisons; 
		possibility of selecting how many? with a bit field? 
		but then we don't get packets at a regular rate. hm, bad.
		Minimum: want threshold crossings every 1ms. 
		Want to frame the packets into groups of 8, at whatever rate needed. 
		If we were to transmit 4 continuous channels, would not need to transmit
		threshold crossings every time, or not the whole threshold crossing. 
		Possibly a simple way of doing it would be to make 1 packet per group of 32 
		channels, and have the same channel active on all 4 digitizing headstages. 
		The radio would be much more used then - currently in use for 1.5ms out of 
		a 137Hz frame rate = 7.3ms.  Quadrupling the bandwidth means that we'd 
		want to do frames of 16 packets - still within the nordic's spec - 
		so 3ms frames in 3.65ms frames. should be sufficient rest. 
		This will also be better use of wireless bandwidth -- good. 
		Can put the switchmode converter by the proc - also good, the wires tend to break.
		Seems like we need to put the proc at 320Mhz - presently using ~1.6us of 2us. 
		Extrapolating, thats 800ns / 1us @ 160Mhz, 64 channels sampled at
		1.066us / 1us @ 240Mhz, 128 channels. might - just might - be able to make it, 
		provided data parallelism can be exploited.
		320Mhz probably requries a core voltage of 0.9 or 1.0V - more power. 
		The present proc uses 17mw - nothing! ; 
		According to the analog devices data, a 300mhz BF532 consumes 63.5mA from 0.85V
		supply; this is 54mw.  Assuming local linearity, that's about 57mw at 320Mhz.
		+ about 7ma leak = 63mw ;; 17*4 = 68mw.  So, a wash.  
		Less space consumed though.
		Also, actual current consumption is less than the Analog Devices data suggests.
January 25 2011 - 
	* Having problems getting RX SPORT0 working on the EMG board. 
		Have tried *pSPORT0_RCR1 =
		* 0x6603 - triggers IRQ, bus contention on both the RFS line and RCLK. 
			So the pads are connected under the chip!
		* 0x4003 - internal clock, external RFS, RFS not required.
			triggers IRQ.
		* 0x4403 - internal clock, external RFS, RFS required. 
			triggers IRQ.
			bus contention on RSCLK0.
		* 0x4401 - external clock, external RFS, RFS required. 
			Nothing. 
			changing RCLKDIV seems to have no effect.
		* 0x0401 - external clock, external RFS, RFS required, 
			trigger on negative edge of clock.
			Nothing, again.  
			The issue is the clock! perhaps cannot work with gated clock?
		* 0x2401 - external clock, external RFS, late FS, RFS required,
			trigger on negative edge of clk. 
			Nothing. 
		* 0x2403 - internal clock, external RFS, late FS, RFS required, 
			trigger on negative edge of clk
			Triggers IRQ!  
			It must be the clock... whaat? why?
		* 0x6001 - rising edge, RFS not required, external FS, external clock.
			Nothing.
		* 0x6201 - same as above, internal frame syncs. 
			does nothing - the frame sync signal kills the clock!
		* 0x7201 - same. 
	FIX!!!
	MUST NOT GATE THE RSCLK signal -- it needs to be running all the time!
	Using 0x7401 -- looks okay, but the first bit is not being latched. 
	This means that everything is gained by 2 .. hmm. 
	The surprising thing is that the ADC produces data the instant FS and 
	CLK go low. 
	Basically need to get the frame sync 1 clock sooner? 
	or use the L/R clocking? That's worth a shot!
	-- did not change much ; data is still shifted over by 1.
	Let's put the ADC in ground-referenced mode.
	Was bipolar: 0x2801
	New: 0x3c01 -- still looks like 2s complement. 
	Tried temperature sensor: 0x2c01 - works, can detect temp fine!
		(used a pressurized duster to change the temp)
		This implies that the input word is formatted and aligned properly.
	Compared the oscilloscope with register contents - the SPORT is reading
		in properly aligned data, at least the bits 0x364? match!
	Let's try removing the external ref-generating circuitry.
		I think that's introducing gain.
		Nopers, it's necessary for the rest of the circuitry. back in there it goes.
	** the first data bit (MSB) is clocked out on the falling edge of CNV
	(TFS0 / RFS0) - not on the first clock edge. 
	Hence, we are missing it! 
	need to delay the transmit data, and have this update on the rising edges. 
	and hope this does not violate setup/hold requriements.. 
	Anyway: Converter latches on rising edges of clock, hence data 
	(and frame sync) should be driven on the falling edge. 
	output register latches on both the falling edge of CNV and clock, 
	hence really need this hooked to an SPI bus..
	If we drive the frame sync on the rising edge of the clock .. no that won't work.
	Try driving RSCLK directly, keeping it synced.  
	yea, that should work. two phase clock.
	TSCLK0 output data latched on falling edge, as config register wants; 
	RSCLK0 latches data in on rising edge, as the data register is latched
		out on falling edge. 
		This implies that rising edge of RSCLK0 must be a little after 
		falling edge of TSCLK0.
	That's not going to work either -- really need RSCLK0 to control
		the DAC, and everything else to be on a phased TSCLK0. 
		will have to change the wiring.
		Done!
	Ok, finally fixed everything. 
	How? 
	Let's review the operation of this chip. 
	1. Configuration register is latched on rising clock edges. 
	2. Sampling starts on rising edge of CNV. 
	3. Clock and serial lines must be silent during conversion. 
		During this time CNV high.
	4. MSbit from ADC is clocked out on falling edge of CNV. 
	5. All following bits are clocked out on falling edges of CLK. 
	6. Hence, you need 14 + CLK edges for the config register, and 15
		to read out contents of ADC. 
	7. This is the simplest operating mode for the ADC - there are 2 others, 
		but the specsheet sucks, and I couldn't decode how to set them up.
		The operating mode corresponds to RAC on page 25 of spec sheet.
	Now, the solution:
	1. Config data latched out on falling edge of TSCLK0, along with TFS0.
	2. TFS0 tied to CNV. 
	3. RSCLK0 ORed with TFS0 to generate gated clock.
	4. RSCLK falling edge slightly behind TSCLK falling edge by inserting 
		SSYNC instruction between enabling the SPORTS. 
	5. SPORT0 RX data latched in on falling edge of internally generated 
		RSCLK0. 
		Hence, first falling edge latches in MSB that was presented upon
		falling TFS0 / CNV / RFS0. 
		Because of the propagation delay through OR gate, 
		this does not violate setup/hold violations. 
	6. SPORT0 RX configured for late frame syncs; early frame syncs miss the 
		first bit. 
	7. Because SPORT0 RX is configured w/ bit 14=0 
		(latch data on falling edge of clock), and TX is inverted
		(latch out data/frame sync on falling edge of clock)
		start RX /before/ TX!

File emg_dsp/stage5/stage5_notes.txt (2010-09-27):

errors in the schematic
1 - DR1PRI is not brought out, most likely b/c it was too hard to route. next time, 8 layers!
2 - no electrolytic capacitor needed.  battery + ceramic is good enough.
3 - need caps on all parallel-port driven inputs / outputs (especially the _cs - 33 or 100pf).

notes from debugging stage5. 

August 3 2010 -- 
	Got it booting to USB; no serial port as I bought the wrong ADUM3202 package.
	The secret is to disable Vcc - processor internal voltage - while programming!
		(should have thought of this before)
	seems quite a bit of current is being dissipated on the 3V supply - 
	perhaps there is a short somewhere? 
	seems more likely to be an open circuit than short, as the solder paste volumes with the 
	Pololu stencils are small. 
	Hmm. What is connected to that net?  Just the RHA2116s - perhaps I've got them 
	hooked wrong, and a diode somewhere is dissipating the current? 
	Let's see if the power disipation is within spec. 
	it's dropping ~ 1.75V.  Each RHA2116 should dissipate 5mw -> 
	10mw, or 3.3mA.  say 3.5mA.  the regulator should hence be dissipating 6mw. 
	It is almost certainly dissipating much more than that!  why? 
	Also, the gain seems low. 
	
	Another mystery - DR1SEC is oscillating.  It should be driven by the ADC7476.  wha? 
	(oscillations perhaps because of a bad ball connection below the blackfin?)
	Checked it again, and it looks okay - there is an error in the schemactic, noted above.
August 4 2010 --
	Intan chips still consuming too much current. Tried reflowing them, 
	no clear change.  Also reflowed the blackfin; seem to have resolved some open 
	ckts there.  
	Intan chips - specifically the 3.0V LDO - get hot independent of the presence 
	of Vcc or Vdd.  (1.2 and 2.85v, respectively).  
	One thing to note: I think it's isolated to the bottom chip. The top chip shows normal 
	bias voltages across the three bandwidth-setting resistors. 
	I'm going to ignore the bottom chip and work only with the top one. 
	So: let's get the wireless working. 
	no, no, first get clean samples from the headstage. 
August 7 2010 --
	Removed the bottom intan chip.  3V LDO no longer dissipating tons of heat = good. 
	I seems that many of the inputs to the intan chip were not connected - 
	Namely pins 1-10, excluding pin 9. 
	Hence, only DVdd and DGnd were set - which is why the chip was heating up so much. 
		(This implies that the other chip may have open-circuits underneath, too!)
	Still have strange sampling-locked noise on the input of the ADC. 
	According to the schematic and layout, there shouldn't be anything else connected
	to the muc pin - ??
	The input to the ADC is a square wave that goes high the instant RFS goes high, 
	and falls 6.4us later - about 3 bits before the conversion is done. 
	Perhaps the ADC is a bit broken... ? e.g. there is leakage when the track circuit is enabled?
	Bottom ADC shows the same waveform, but it's not connected to anything. 
	----
	Anyway, input referred noise, with the input hooked to the plexon artificial rat
	is 10uV RMS.  This was measured by recording via USB, lowpass filtering to 5khz 
	(sampling rate set to 100ksps), and taking the std. I think this is reasonable?
	----
	Supply voltage are all close enough to not turn on any ESD protection diodes, I think. 
	RHA2116 is at 3.018V. 
	ADC is at 2.701V
	Blackfin is at 2.872V. 
	The biggest difference is between the ADC and RHA2116, which is still only 300mV - 
	and the connection between them is just signal and ground. 
	----
	Let's test the gain. Input signal 4.5V pk-pk.  after plexon -> 450uV pk-pk. 
	hum.  I don't see a sine wave. that's not good. 
	Yea, I can't find the signal via fft, either, though it seems to be there on the 'scope. 
		(with a good bit of noise from the sampling-locked noise mentioned above). 
	The noise amplitude is about 100mV; the signal amplitude is approximately the same. 
	Input-referred, that's 500uV, okay, chip is probably working. 
	the SCK signal seems to be coupled to the input of the ADC, with 
	the ADC off (no clock or frame sync) and the muliplexer off (no step signal). 
	Let's look at the layout for that. 
	There is no good reason for the two to be connected - 
		they are not so close together in the layout; must be connected through input amplification?
	This appears to have been a result of an open connection on the board.
	----
	Reflowed the board, put the 'broken' RHA2116 back on - now it seems to work. 
	Unfortunately, the omentics connector fell off in the process. 
	The problem is clearly the SOLDER PASTE- too little, and it does not wet the devices well 
	(the nRF24L01 may have some open circuits, and it's interfereing with the flash - 
		could try reflowing that if i want to destroy more shit)
August 9 2010 --
	reflowed the radio. board does not even get past the manufacturer ID without nRF24L01
	on there!  Radio does, however, seem to be soldered corectly - at least now. 
	reflowed the blackfin, again; perhaps there is a cold joint, but all pads and balls 
	appeared to have solder / solder paste, so there (theoretically) should be no open-circuits. 
	there is also the possibility that traces within the board are broken; will need to make another.
	----
	blackfin shorts Vdd. removed it; observed too much solder paste under the balls. 
	will have to decrease apeture of associated solder paste mask.
	behavior of the board without blackfin: still errors in writing the flash. 
	specifically, the last segment of the first page is all zeros. 
	modified the program, and now get the stuck-byte problem: same byte is written to flash
	(or read from flash) for many memory locations in a row. 
	Looks like it's a memory read error - the pattern changes with two serial reads, 
	though the error seems to start around the same point.
	Weird, I do it again, and the read seems repeatable, with only 2 errors - and the errors are 
	consistent. 
	And now it all works ??!! what the?  Must be a flaky connection somewhere. 
	Perhaps the level translators? hmm. Flah voltage is correct, in any case. 
	-----
	Trying to test communications in the simplest way possible - requesting the flash to ID itself, 
	over and over agian. 
	At first, it wouldn't work, but now it's quite reliable. WHY??
	It looks like interupptions to the power are sufficient to cause strange and undesired response
	post-query - let me try removing the electrolytic.
	YES that fixed it.  why, oh so why? 
	Also to note: 
	* removed printf statements during program sequences. 
	* killed X.
	Need to mantain constant clock rate!! 
	Now, put the blackfin back on there, I guess.
	Done.  works!  comes up as /dev/ttyUSB0 !
	Both Intan chips appear to be working, despite all the reheating I've done to them! 
	----
	Next, to measure the signal and noise quality of the digitized data. 
	Don't have an omnetics connector on there - in a box, it's 23uV RMS noise.
	Not too bad for no input and possible contamination from USB. 
	need to test this with input shorted, I guess. Or, better, a real input. 
August 10 2010 --
	reflowed the nRF24L01 twice, the PA supply was not connected. works now, apparently. 
	check the data. 
	Now the flash isn't coming up $%^#!
	** Need caps - 100pf maybe - on all the parallel-port driven signals!! **
	finally - everything seems to be working! Need to debug the packetization. 
August 11 2010 --
	Debugging packetization: is it the write or the read? 
	Disable write; fill buffer up with known pattern. 
	looks like we are missing packets? No, the interrupts indicate otherwise. 
	start byte = 
	00, 40, 80, c0 (repeats 4 times) 00 c0 80 40 80 c0 
	another trial: 
	20 60 a0 e0 (repeats 8 times) a0 60 a0 e0 a0 60 20 60 a0 e0 20 60 a0 e0 20 60 a0 e0 20 60 a0 e0
	Ok, first task is to determine why every-other packet is dropped. 
	pretty sure it's the USB. yep, fixed!
	now need to check fidelity, I guess - matlab.
	matlab: looks like within a packet, everything is in order, though packets may come out-of-order.
	is this a programmatical error, a USB error, or a radio error? 
	The pattern seems to be repeating: 8 clear ramps, unordered pkts, 
		8 clear ramps, unordered pkts, ditto, 
	1 ramp = 256 bytes = 8 packets. Let's make sure it's not the USB, then.
	It is USB! write a known pattern via SPI, and it appears the linux kernel reorders them. 
	This is at the relatively low rate of 8 packets every 17ms -> 14.3kbytes/sec (115kbits/sec). 
	Hum. may have to timestamp them on the radio-> USB bridge. or just fix the problem.
	Another thing: looks like there are unequal number of instances of each octet. 
	In a 640 packet stream, some are 76, some are 86. should be 80. 
	Perhaps this is because the packets come in bursts?  Would buffering them help?
	Upon noticing that the SPI clock was still running after nRF_CSN went high, 
	tried switching from DMA-controlled SPI read-in to processor control 
	- no change in transmitted data, though, still unordered packets. 
	Looking at the USB_IRQ right now, and it's pretty clear that we are overfilling the output 
	buffers during a radio burst - doh - sure would prefer ethernet here! 
	Maybe next time i use a FDTI device? Ugh, re-engineering. perhaps ethernet is better.
August 12 2010 --
	Using libusb to read from the device; works much better, though the packets seem to be
	reversed within the read.  I'm not sure why.  The bytes on the wire are, at least according
	to the /dev/ttyUSB0 interface, in order.  
	Bytes within the 64-byte packets are in order, however. 
	Diff(recorded data) has only 3 values: +129, 1, -127.
	Reversed packet order is independent of buffer length 
		- at least for lengths 64*16 or 64*4 bytes.
	Changed this, no idea why it would be reversed, but easy fix. cough, Fixed!
	----
	Next, the radio. uh - it's back to being disordered. - seems to depend on initialization?
	Tried it again, looks good, no (none!) errors! this means the radio tx code is good.
	----
	Now, can use this to debug continuous data (not just ramp) transmission.
	Turned back on p3 (WFBUF write pointer). 
	Does not look correct - samples are saturated, 0xfff5; 0xbaadc0ed occurs aperiodically
	intervening bytes: 56, 12, 56, 132, 104, 64 ...
	ah, was writing *words* (16 bits) not *bytes*.  now it looks good, only the samples are 0xff..
	seems that there is ~1 lsb of noise in the system.  humm.
	channel 1: all 0x91 0r 0x91 lsbyte. 
	channel 16: all 0x98
	another problem: tx chan only goes to 16.. ? ah, that is correct given the code. 
		fidelity looks fine with this; removed the packet reordering; why did we need it before??
	note!!  seems you can only write to a full register when reading from the serial ports -
		e.g. r0 = w[p0] (z) ; 
		that's silli!
		but now the signal looks okay (from only one of the chips - the bottom - the top one is hot)
	----
	finally, got the radio working properly - at least to some degree / resolution. 
	now it seems that whenever there  channel is changed, there is a good bit of noise on the output.
	but .. not always, not on all channels.  perhaps only on the channels that are floating? 
	see http://m8ta.com/index.pl?pid=839
	Seems to be the radio - artifact is clear when PA turns on.
	No!  radio transmission disabled, PA disabled, SPI still active - strong artifact!
		(this means that there is / should be sufficient isolation between radio and input. 
		that is not to say it couldn't be larger - !)
	SPI needs to be re-routed here, we need it to boot, etc.  shiiit. 
August 13 2010 --
	Reflowed the top RHA2116 - still does not work.  consumes a lot of power. 
		Bummer, I was very careful this time. 
	rerouting the MISO line & grounding the existing trace seems to fix the interference problem.
		On the next revision, need to *not* do this!
		Anyway, can debug filter.
	Let's looks at this again: data comes in at 12 bits.  have 15 bits plus sign of headroom - 
		so total gain through the filter should be 16., or 2 per biquad.
		(have 4 biqads to work with).
	First biquad = okay. 
	Second biquad = saturating @ 0x7f.  shiit.
August 15 2010 --
	Figured out the filter problem - had a += instead of = on the b[0]*x multiply. oops.
	Now the output is oscillating back n forth every 1,2,3 samples
	Seems to occur after 2 biquads - checking with just FIR filters. looks okay.
	try leaky integrator?
	yes, that works - but after a while sharp edges re-appear. not sure why. 
	looks like some part of the recording system - perhaps the USB - is getting hose'd . 
	Seem it shifts into and out of proper ordering -- but why? 
	Seem not to be the filters themselves. 
	No, rather it seems we are dropping packets predictably - after making a sine wave generator, 
	see that there is a pattern to diff(b3).  hummhum. mysteries abound!
	decision: usb sucks, use ethernet. yesyes yall// and I've got the EMG board right here!
	another decision: move away from the maxim chip, and toward FTDI 2322H.
August 16 2010 --
	Time is running out before the next trip. What is the most efficient use of my time? 
	Redesign the board & get it shipped out by .. Thurs?  Not likely, given the complexity.  
	Well, is the USB bug irrecoverable?  can we figure out what is causing it, and fix?
	I presume it is because a USB packet is being overwritten while in the outgoing fifo.  
	(this same problem again... damnit). 
	Buffer the outgoing data? in a circular buffer?
	Need to check to see if the outgoing buffer is emptied -- yea, the IN2BAVIRQ bit.
	okay, fixed that.  are we completely sure that it's the USB and not radio? 
	better check with ramp.
	yea, we still get errors with the ramp - occasional jumps of 65, which corresponds to 
	lost USB packets. damnit, gina! 
	This seems to occur very consistently after the start of a new ramp. 
	radio packets are 32 bytes, 8 of them -> 256 bytes, same as wrap period of ramp. 
	so jump occurs on the second radio packet - i think? 
	It jumps from -111 to -46.  hum, might have a 16 offset here in the ramp signal.
	BUT, the error only occurs every 4th frame - and this is consistent.
	perhaps it is the reading program?  this is 1024 bytes, which is what the buffer is set to.
	try smaller buffer.
	NOPE, it was a bug in the recording program.  USB works perfectly now!! YAY. 
	test with radio -- much better. still, some dropped packets, but not so bad.
		16 in 140samples = 16 in 5028 samples = 0.0032 error rate. hm. could be better?
		perhaps my radio is imperfect?
	With radios right next to eachother - 
		37 dropped packets in 12734 packets = 0.0029 error rate. 
		Assuming that chksum discards in case of one error, this is a BER of 1.1e-5
		could turn off checksumming.
	Okay, what next? filters, test the filters.
		filters don't look good - not smooth enough, not enough lowpass action
		(compared it to the same result computed in matlab). 
		First lowpass is certainly not working -- lots of fs/2, fs/3, fs/4 noise.
		period is not correlated with digital pipeline - 208 samples, def. 60hz noise.
		sign of the coefs? hmm. 
		Tested design procedure in matlab, filter works as expected (w/ some phase delay)
August 17 2010 --
	Testing the filter; seems to have the correct sensitivity to the different parameters. 
		(at least for sine wave generation). 
	Now testing impulse response.  Definantly different! In matlab, the main pulse is 6 samples.
		In blackfin, 4 samples.
	Looks the same in the C fixed-point test. 
	after fiddling with the coeficients, looks like B tapped delay is not right!!
	Reimplemented it, still messed up - guess I'll try pure FIR? 
	Waaaait a second, this is pre-downsampling!  of course we're missing the middle sample. 
	D'oh. 
	Also: looks like we are saturating. really need AGC. otherwise, impulse response okay (for lp)
	with all filters, the impulse respones looks fine. Test with realish data. 
	Hmm.  try turning down the gain?
	Nope, looks like the filter output is correct. 
	Also -- seems like butterworth filters behave better on the real data than elliptic.
		better phase characteristics.
	Well, anyway, what's the next task?  I guess get the thresholding --
		and decide if we want incoming bandwidth. Probably, yes.
		Needn't be much - one packet after every frame? this will make 
		the radio routine longer :-/  well.
September 10 2010 -- yesterday got the device fixed at Protronics; looks good, both chips working now!
	Also they soldered on the omnetics connector again. 
	now working on bidirectional radio protocol, but it seems that when transition into RX mode is 
	included, transmit IRQ is no longer present -> not sure why? 
	test: longer delay after CE is de-asserted. 
		try 16us delay after de-asserting CE -> no dice. 
		32us de-assertion after both transitions -> nada.
		clearing IRQs before RX -> TX transition = also no effect.
		disabling the PRIM_RX bit makes it work!  hum.
		putting it in power-down mode between transitions: yea, that works!!
	Actually, it seems that it's a BAD IDEA to change the IRQ mask bits in-flight - huh! 
		best to leave both RX_DR and TX_DS bits un-masked.  not sure why -- ? 
		(MAX_RT (retries) is always masked). 
		And putting it in **power-down** mode is essential...
		.. the delay after de-asserting CE is not essential.
		.. flushing the TX fifo is not needed.
		(I'm not sure why my notes (comments in spi.c) indicate that transition to 
		power-down mode is not needed - ? 
	Well,i  guess it's time to get the other end working.
	-- Discussions with Zheng: how to sync the two sides?  The bridge needs to know when 
	to send commands (hum, that said - need a better way of communicating, USB  <<< ethernet. 
	ugh, don't want to make another board?!!  perhaps can populate emg_dsp?  might want to check.
	Whatever.  Can use a bluetechnix iMX.51 maybe, although this is overkill. 
	-- Let's look at bandwidth.  continuous transmit of one channel, 27 samples + 1 flag byte + 4 threshold 
	bytes.  Data coming in at 1msps / 32 = 31.25ksps / 27 bytes/packet = 1157 packets/second. 
	= 144.67 frames/second. 
	Expressed in bits/sec: 
		296 kbps outgoing.  
		37 kbps incoming. 
	without flag/data byte: 
		285 kbps outgoing
		35.7 kbps incoming.  -- not too much difference, might as well sacrafice! 
	alrighty -- bidirectional seems to be working!!  with real data, too.  great. 
	Next: incorporate the actual sample / filtering algo.  hopefully we don't need to re-write the damn thing in C. 
September 13 2010 --
	Thinking about the filtering again -- it will be hard to completely change the system, 
	as there are 2 weights per 32-bit word, and these weights are shared between 2 simultaneous channels. 
	making each channel have its own set of filter coefs would increase memory read bandwidth by 2. 
		this may not be such a problem - really is only one more memory read per biquad. 
		actually, it looks like we can have completely different filters per channel, no problem!
	also, each biquad has relatively little capability for gain - 
		for very small signals, probably have to distribute the gain.
September 14 2010 --
	Looked over the code, and - surprisingly - it's all basically working.  looks fine when the bridge is off, 
	but when the bridge is on looks like we are forgetting a clear-interrupt? 
	no not really -- seems that every other transition is not working. 
	specifically, transition to TX mode?  hm.
	This is dependent on the bridge transmitting a packet 
		-- if it's turned off, output looks good. (8 packets, all good)
	Aha!  looks like i was forgetting to terminate the CSN frame on the RX read-packet. oopsie.
		now communication looks good - except for the fact that the channel is not getting through? 
		ah, fixed.
	Next: the samples look like shit; probably the filtering is not working.
	Raw samples from ADC look fine; therefore, yes it must be the filter.
	First filter stage looks okayish - mostly 0xc_ or so.  0x11-- ----.  really need a program for looking at this.
		ah, I've already got pthread in there for display! nice. 
	Okay, looking at the data - direct, pre-fitlering: there is noise. looks like it's sourced from the ADC? 
	(tested with constant output in code - it's clean!)
September 15 2010 --
	Okay, first: diagnose the noise corruption.  
	The zeros in the data stream do not occur when the device is on battery power, 
		disconnected from programmer too. 
	The noise occurs 8 times in a buffer of length 64 * 32 = 8 frames. 
		makes sense, as the duration of the noise is consistent with SPI writes. 
	So, the noise is either from the SPI bus, or from the radio (i'm leaning toward the SPI bus..)
	also we need to be able to write to the bridge - to allow us to switch channels, e.g.
	first biquad looks okay (lowpass). 
	actually, all the filters look like they are doing their job. good! 
	now, we should try to permit filtering changes (gain etc) from the computer. 
	getting there ... looks like need to debug the bridge. 
	yes: after you send a packet, seems that the radio is not emitting all IRQs. this is independent of USB activity.
	removing the code that reads data in from EP1 fixes the problem - 
	with the caveat that the write is blocking. 
	if we just write one to rEPIRQ, bmOUT1DAVIRQ, works okay.  perhaps we are not using ACKSTAT properly -- 
		these are bulk enpoints, not control endpoints.
		yeap, don't need to call wregAS!
		also don't write anything out on the UART.
		fixed! now - why is the channel not changing? 
	Looks like the packet sent to the headstage never changes.  why oh why?  it was working a sec ago.
	problem: was sending full 64-byte packets over USB; should have sent 32-byte packets.  fixed!! 
	now we can change channel! 
	Next job: adjust the gain of each channel. 
September 15 2010 --
	Changed the bridge to run at 400Mhz.  no change in the packet-loss issue: 
	looks like we'll need a more complicated protocol for transmitting data. 
	Strangely, when i had inadvertently disabled the PLL, and the chip was running really slowly (not keeping up with data)
	there seemed to be no lost USB packets.  yea right! 
September 20 2010 --
	Got the filtering working better, but reset filter coefs still not working perfectly.. this is v. tricxy! 
	looks like the damn filter is oscillating - changing the gain does not affect the resultant sine wave.
	Need to make the USB ultra reliable -- seems that the packets are being re-ordered?  
	I've tagged them with unsigned integers, can use these to re-assemble. 
		this did not fix anything .. wha? 
	Tried it on the faster computer (loco) -- no difference. must be dropped packets? 
	what happens if we turn off CRC on the radio? 
	still works perfectly. 
	now generating a sine wave on the headstage, with no CRC; sine waves look uniformly perfect on the screen, 
	BUT this just means that USB is droppping packets -- we are assembling packets in the program 
	depending on the earliest / first packet found in a given take. 
	Hence, need to have a bidi protocol for reading from USB, where we can reset the read pointer where needed.
	** I think it's the bridge -- the beat is periodic. let's plot with hex..
	yes!  it seems that there is not enough outgoing bandwidth from the bridge -- the 
	if(write - read) block is being triggered, causing the appearance of dropped pkts. 
	however! during the actual transmit seq, no packets seem to be dropped - 
	this is all a matter of proc speed? changing the # of printfs does not seem to change things. 
	incoming data rate 296kbps. 
	that's 37 kbytes/second
	packets are 36 bytes, serviced every 1ksps -> this is presumably why we get skew.  yet yet.. 
	what happens if we buffer them? expand the packet to 64 bytes? 
	seems like we're just going to have to write full 64-byte packets out. bummer, i guess. 
	it is seemingly certainly the outgoing b/w that is the problem.. bweh.  perhaps the spi bus? 
	well can't really tell ... could try increasing the clk rate. 
September 21 -- starting a new board!  this one will have proper ethernet and USB2. horray!
	blackfin BF527: both ethernet and USB OTG, 132k memory, mobile SDRAM. 
	BF547: usb OTG, mobile DDR, lots of peripherals, many many pins. 
		also looks like you need resistors on the DDR interface; 
		gluing to an ethernet controller is probably not too bad. 
		use a M25P16 SPI flash. (16 Mb) (?)
September 22 -- designing stage6
	wired headstage:  might as well as use a 16-bit ADC.  40ksps * 16 channels = 640ksps. 
September 23 - to add: audio out on EMG board.
	audio out on bridge, too! 
	The LPC111x series may be better - about 8-9ma dynamic current draw @ 48Mhz.  
		and we don't need to overkill with the EMG - fewer channels, lower sampling rate (4khz per channel). 
		That said, the blackfin works pretty good, and I'd prefer not to have to make / learn a new toolchain.
	Total power consumption, static: 
		750uA / inst amp MAX4208.  5V -> 30mW. 
		OPA4348: 2x, < 3mW
		ADC, 0.7mW
		radio: 11.2mA, 2.5V, 16ksps @ 16 bits -> 32kbytes/sec, 256kbits/sec, + incoming -> about 4mW.

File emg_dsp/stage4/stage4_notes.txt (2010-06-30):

---- board fixes ----
1.  Mounting holes are still too small for standard 4-40 machine screws. 
2.  FAN2001 footprint needs to be tweaked - EP can be smaller. 
3.  Make sure to use LARGE DOME BUMP LMV1032s. 
4.  SYNC_IN pins need to be connected together per channel to avoid excessive 
	beat-frequency noise. 

---- solder paste mask notes ----
1.  Solder paste apeture for LMV1032 should be 13 mils: 
	%ADD20C,0.013000*%
2.  Solder paste apeture for TPS62410 should be %ADD29R,0.110100X0.030400*%
3.  Remove holes - D51 in the present output.

---- electrical testing ----
1.  Feb 26 2010 - Testing the 74HC467 to see if it will switch quick enough to 
	multiplex for the neural headstage at low supply voltage; the datasheet warns 
	that the switches are very nonlinear at low voltage, but nonlinear is OK
	so long as the output settles to steady stage in time for the ADC to sample. 
	Anyway, to sample 16 channels at 50ksps each, need to switch at 800kHz. 
	First, we test at 3.15V (two AA batteries)
	Set my function generator to that -> looks good, especially to ground. 
	The slew rate is actually higher than that from my function gen!
	Should test to Vcc/2, since per the spec sheet that appears to be the area 
	where the multiplexing switches are the most nonlinear. 
	With one input to the multiplexer at 0 and one at 1.5V, there is about 75ns
	of ringing on the output/common line. Not too bad! 
	Now, test at 2.45V (one alkaline and one NiMH battery): 
	Still looks good!  There is about 75ns of delay, but little ringing, and the signal
	seems to settle to the steady point very quickly. 
	Indeed, the multiplexer seems to behave well even with the address lines
	toggled at 2MHz.  I wouldn't use it that high, though.  
	Slew rate at Vdd=3.15V about 1.5v/20ns; @ Vdd=2.45V about 0.8v/20ns.
	----
	Conclusion: NXP's 74HC467 will work well at 2.7V multiplexing signals
	with the address lines changing at 800kHz. 
	
2. March 30 2010 - The Shutdown (SD) pin on the MAX253 is not driven - 
	Should be connected to ground, or so. 
3. All the voltages seem to come up correctly (after I reflowed the damn little 
	TPS62410 - internal short to center pad).  Next, thes out the microstim channels? 
	Or try flashing the device?  need usb.h in svn!!
4. Processor does not boot - no data on MISO lines.  (There is data on MOSI and SCK)
	PF2 is high - why? perhaps a short somewhere? 
	hmm... after a bit of probing, it seems the proc is booting! 
	(maybe I disloged some bit of old solder paste?)
	and the serial port is also working.  horray!  can use this for debugging. 
5. Next thing, I think, is to get USB working, then maybe write a stim program. 
	Nah, let's check the AFE. 
	Looks like something is shorting the output of V18 LDO -- it's only ~287mV. 
	Trying to reflow the thing -- better be careful though! 
	Hmm.  These chips are really hard to work with ... but managed to fix the problem by 
	removing mis-placed chips & applying current. 
6. Check the gain:  4.5V in -> 450uv -> 1.5V out :: gain = 3k.  hmm, a bit high. 
	Well, anyway, the multiplexer works - at least a few channels of it. 
	Let's read them in via USB. 
7.  uclamp501 was oriented in the wong direction.  It has a bar - treat it as a diode!!
	Just remember that on the PCB, pin 2 is the anode. 
8.  Still having problems with flashing and booting the device - sometimes it works, 
	sometime it does not!  this *needs* to be resolved. 
	Also - and perhaps more importantly - the thing does not always boot! 
9.  When I output a ramp, USB transmissions are all correct, in order, the right size etc, 
	however! when i output actual samples, the file is read for a few sampels - say 100 - 
	then fread dies.  why?  is it in the data, or is it in the code / data dependencies in the 
	code? 
	-- If the device is not transmitting data, then the fread blocks, as it should. 
	Input, 2V sine wave at 1.5kHz -> 800mV sine wave on MUXA 
	(gain = 4000, okay as the THS provides a bit of extra gain)
	(this is equivalent to 200uV signal on the input)
	signal is clear in the sampled signal, amplitude ~= 900 samples. 
	minimum input size that is detectable on MUXA: 140mV pk-pk square wave. 
	(14uV at input - okay, but not great). 
10. Actually, it looks like some of the DAC signals are being driven onto the THS opamp's 
	output - uhohs - let me check with the DAC disabled (this sychronous noise should 
	ideally not factor into the ADC codes..)
	ADC off, 1.5khz sq wave in -> MUXA pk-pk = ~144mV
	ADC on, same input -> 156mV.  hmm.  that's actually a good bit; would be nice to get rid of it! 
11. Input-referred noise: 220mV @ DAC => 55uV.  w/ 500k source resistance. 
	Source shorted: 120mV @ DAC => 30uV.  note this is peak-peak!! 
	If we use the scope to measure RMS values, I'd estimate it to be 25mV -> 6mV 
	input-referred noise, input shorted to gnd. 
12.  Well, anyway, I guess the analog section works oky - will need to test on a rat/mk, but 
	first need to get the radio working?  or figure out why it does not boot reliably? 
13.  Radio seems to come okay - at least can read and write through the SPI bus.
	I'm tempted to try to get 'normal' SPI working - e.g. so that we don't have to manually toggle the 
	PORTF flags & ssync.  eh, later, it works now!   (radio output is not verified - need another 
	radio for that!)
14.  Boot problem. Seems to boot perfectly when USB is not connected. hmm. Perhaps a radio issue? 
	Weird as hell... hmm. I'll try turning it off for a while, then come back and see. 
	Boots properly. good, but not good for debugging - ?
	I guess I'll just order parts from mouser for 3 microstims. 
15.  EMG: Testing the EMG electrodes with Jon and Prashant; need to increase the spacing on the contacts, 
	relatively simple fix but needs a board revision.  
	This should make it so we record more units -> more voltage output -> more informative signals.
	Jon suggests 1/4" diameter stainless-steel dome electrodes.
	The recordings, as well known, are very sensitive to ground noise - we need to decrease 
	ground connection impedance & increase reliability - maybe a conductive fabric elastic belt?? 
16: microstim: tried wiring all SYNCIN pins together, seems to help with the noise; 
	there is still a nastish bit of switching noise on the output; I think the solution is to
	synchronized them all together, with 4 phases, via the processor.  
	As long as the noise is above the highpass frequency of plexon, it doesn't matter. 
	(Provided there is no nonlinear/AM type demodulation)
17.  June 11 2010 - testing 3 x LMV1032-25 in series, total gain 75db = 5623. 
	Input decimator 33k / 27 = divide by 1222. 
	Input voltage: 79mV RMS -> 64uV @ input. 
	output voltage: 650mv RMS _> total gain 10,000 (??)
	This at a frequency of 1kHz; also tested with 3khz, same numbers. 
	Seems RMS calc is inaccurate on the scope with noise; try again. 
	Output noise: 144mV pk-pk. 
	Output signal: 656mV pk-pk with 124mV input prior divider -> 100uV pk-pk
	hence, total gain = 6500, which is close to the expected value. 
	Input referred noise is then: 21uV pk-pk.   This agrees with earlier measured values (30uV, #11)
	Note amplifier is running off of two AA batteries, 2.5V. 
	There appears to be little dependence of noise on voltage above 1.7V.  
18.  Bandwidth measurement of the 3 LMV1032-25: about 50Hz to 22kHz.  
19.  The other worry is input offset - can't test with the current setup, as the offset voltage is / 1222 too!
	Microelectrodes can have relatively large offset voltages, which may saturate the amp. 
	The input saturates rather quickly - offset voltage of each amp is only 600mV, 
	which is exactly what the spec sheet says. 
	2 amps do not saturate with 2.25V -> 1.8mV input sine wave. 
	Sturates at about 3.8V -> 3.1mV, and even then seems relatively offset-agnostic = good! 
20. Let's think if we can get away with 2 LMV1032-25s.  That's 50dB gain -> 316.
	With a 2.7V supply / reference, one bit of a 12-bit DAC corresponds to 659uV
	referenced to the source, that's 2uv.  So, perhaps it does not make sense to 
	use more than 2 LMV1032s.  just pass it into the mux and immediately digitize. 
	Accordingly, 100uV spike correxponds to 47 counts.  kinda smallish. 
	With an extra LMV1032-15, that's 268 counts.  Humm. 
21.  Second full build-up works;  put the LEDs in backwards, oops. 
	problem is that you need 2 radios for a communicationlink!  
	Guess I'll have to build up yet another board - must make sure I have enough parts. 
22.  Third full build-up eventually works - had to reflow the blackfin several times/
	Timing signals, especialyl the clock, are ringing - need to put series 
	resistors on these!  
	Stil lhave to figure out how to get correct iming on the ting - ADCS7476 
	wants falling edge of CS 10ns before falling edge of clock; 
	blackfin wants to drive CS (framesync) on falling edge if data is to be sampled on rising edge. 
	Aha!  the datasheet is wrong! THe ADC drives output on RISING edge of clock (and samples CS on rising edge)
	(or at least for the headstage this is true)
	We should sample on the FALLING edge of the clock.  now everything looks good, all samples 
	properly scaled etc! 
23.  Okay, SPI to the nordic is working properly - testing with spi_write_register_ver - 
	But, SPI clock is *not* running during the actual sample loop?  why? 
	(... much debugging later:  somehow i fixed it.)

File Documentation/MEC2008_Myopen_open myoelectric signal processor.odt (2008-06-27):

Leveraging larger markets to encourage innovation in prosthetics: Design of myopen, an open myoelectric signal processor for use as an input device for video gaming and hobby robotics

Timothy Hanson and Jonathan Kuniholm

Duke University and The Open Prosthetics Project

Abstract

The prosthetic arm market is small; perhaps 70,000 people lack arms in the US. This, coupled with the difficulty of making and controlling a mechatronic hand replacement, has forestalled innovation in arm prostheses in the fifty years since its introduction. Since the Boston Arm project in 1965, the popular press has promised thought-controlled prosthetic arms, yet the promises of scientific research have not often been kept in the clinic.[[^1]] We aim to surmount these obstacles by developing an open myoelectric signal processor targeted at researchers, hobbyists, and video game enthusiasts. Our device is capable of processing 16 channels of surface electromyographic (EMG) (or other data), applying pattern recognition algorithms in real-time via a power-efficient Blackfin Digital Signal Processor (DSP), and delivering the results through ethernet, I2C, RS232, USB, and Lego NXT bus. We hope that this open, commodity level platform will become a disruptive technology, encouraging experimentation in the algorithms and applications of a field that has been sequestered too long in the research lab.

BACKGROUND

Much recent media attention about prosthetic arms has surrounded the Defense Advanced Projects Administration (DARPA) Revolutionizing Prosthetics Program (RP2007/2009) and military amputees from recent conflicts. There remains a disconnect between the reality facing an arm amputee and this coverage in the popular press. As of 2007, there were fewer than 700 US military amputees from Iraq and Afghanistan, of whom fewer than 150 were arm amputees.[[^2]] Despite the relatively small numbers involved, the media coverage may have brought a welcome increase in efforts to improve arm technology. The DARPA prosthetic program has been compared to the Manhattan Project and the race to put a man on the moon.[[^3]] While perhaps an apt comparison in terms of the technical challenges presenting the researchers, the comparison of project budgets in Figure 1 shows that the Revolutionizing Prosthetics Program budgets represents a small fraction of the size of those of the two historical projects. The massive historical efforts in fact compare in size to the R & D costs alone of the current F-35 Joint Strike Fighter program.[[^4],[^5],[^6],[^7]]

The deficiency that these programs seek to correct is a basic lack of widely adopted advanced upper extremity products. Many amputees, despite being fitted with myoelectrics, return to body powered designs that have changed little in fifty years. Powered products remain slower, heavier, more fragile and more uncomfortable than the alternatives. This is no fault of the companies that serve arm amputees, but the result of a convergence of factors: the small market size, and the difficulties of the problem of replacing an arm. It is not clear that these realities will make the transition of the impressive technology developed by the RP2007/2009 teams to commercial products any easier. It is this “last mile” of the transfer of technology that we have sought to address with this project.

Figure 1: Budgets (Billions of 2006 Dollars)[4-7]

What is it that separates mass markets from underserved ones? The distribution and therefore lowering of costs, in research and development, manufacturing and distribution to a large number of users. It is also the commodification of products in the marketplace, reducing profit margins because of the availability of alternatives. As illustrated in Figure 2, the buying power in the current market for powered arms cannot hope to challenge that for razors and blades.[[^8],[^9],[^10],[^11]] The ability of these larger markets to overcome higher fixed cost barriers to entry explain the pace of innovation in those areas.

Figure 2: Recent Annual Sales ($Billions)[8-11]

PARASITIZING A LARGER MARKET TO LEVERAGE TECHNOLOGY

Pattern Recognition

While other avenues exist for overcoming these barriers, the one that we have chosen is to seek application in markets with fewer limitations in buying power for underused technology in which we are interested. One of the most promising possibilities for prosthetic arm control is myoelectric pattern recognition. Despite more than 20 years of research in this area, and the advent of prosthetic hands with kinematic capabilities exceeding the possibilities for conventional control, no commercial product in arm prosthetics uses it. In order to help make this or any other advanced signal processing technology more accessible to amputee users (and manufacturer and prosthetist users), we have created a product that makes it possible to use pattern recognition or any other signal processing algorithm on skin surface EMG signals for a variety of applications.

In support of the project, a Matlab code base has been generously provided by Dr. Kevin Englehart at the University of New Brunswick (UNB), in Fredericton, Canada. The software, named CEVEN, contains code written by Dr. Englehart and his students, and was assembled into a single package by Blair Lock. This package provides training, classification of EMG signals through a variety of methods, and visual simulation of arm movements that can be paired with pattern recognition. UNB provides no support for the software, and all support and discussion should be maintained through the Google Code site: http://code.google.com/p/myopen/. Ultimately, the project seeks to port the code to a python or similar high level and free platform, but the Matlab version is available in the meantime.

Using the Power of the Video Game Market

Of the collection of large mass markets shown in Figure 2, that for video games and game hardware is the largest. Worldwide spending is almost $18 billion on items for this type of entertainment. The industry has recently undergone several transformations in human interface, from the use of wireless and accelerometer technology in the Wii controller, to the Emotiv controller's use of EEG signals for “brain control”. Pattern recognition is an obvious very capable addition to the battery of ways in which humans can intuitively interact with a virtual world.

Openness Ensures Access to Technology

To ensure that all stakeholders can actually take advantage of the benefits that come from the use of pattern recognition in the video game market, we have chosen to release both our hardware and software designs under the open source GNU Public License. By ensuring that the designs will always be freely available and changeable, we can break down the silos that separate different uses for the technology, allowing user customization for purposes that we have not yet envisioned.

This approach has been around for a while in software, but is relatively new in hardware. Several current devices use it, including the Neuros OSD video device, and the Buglabs BUG. The multi-purpose linux BUG device with swappable and easily configurable components includes a GPS, touch screen and motion sensor, with which users can make their own embedded devices. Because of the added complexities involved in dealing with the physical world, this approach is still very much the beginning of an experiment.

TECHNICAL DETAILS

Our first iteration of the MyOpen EMG signal processor is based on the Blackfin DSP and has a number of features to encourage development, customization, and interfacing to the greater world. The board for this device is effectively broken into two parts: the digital section, including the DSP and all communication ports, and the analog section. The two sections are electrically isolated for safety.

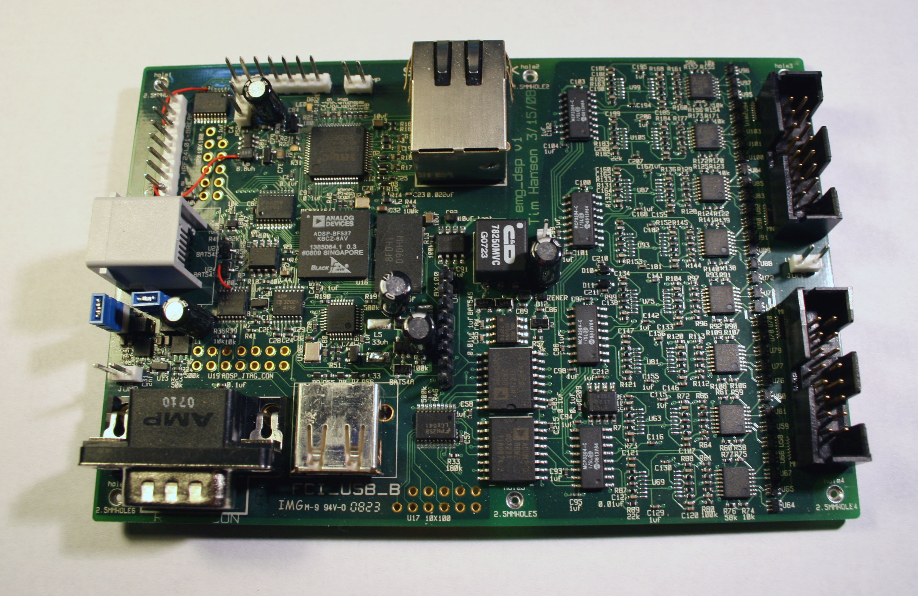
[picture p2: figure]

Figure 3: The MyOpen EMG Digital Signal Processor

The analog section consists of 16 channels of differential EMG amplification. At the head of this signal chain is a low-cost, low power instrumentation amplifier(INA2322) followed by a high pass (fc = 1hz) and a low-pass (fc = 400hz) stage. Both filtering stages are in a multiple-feedback configuration, and both provide a gain of 4; the instrumentation amplifier provides a gain of 30 for a total system gain of about 480 (54dB). The filtered EMG signal is digitized at a resolution of 13 bits with the four-channel MCP3304, and this data is sent to the digital section of the board via ADUM2400 magnetic isolators. The analog section has a 0/2.5/5v split-rail powered via a MAX253, transformer, and low-noise regulator.

The digital section features the DSP, 32Mbytes SDRAM, ethernet PHY & magjack, RS232, USB, JTAG, and Lego NXT compatible I2C / TWI. The board also features a small 128x128 pixel serial LCD for debugging and user interface, as well as header breakouts for 8 general-purpose pins on the DSP. Each of these devices may be powered down to conserve battery power. Furthermore, a low-power pin-compatible Blackfin BF534 chip may be substituted in for the faster BF537 when the ethernet interface is not required. The core voltage for the Blackfin may be runtime switched between 0.8V and 1.2V, again to save power. This and the system 3.2V bus are supplied through two efficient synchronous buck converters from either a 3.7V lithium cell or a 5V external supply.

The first revision of the board is 6 layers, routed on 0.005” trace/space rules, with 0.006” minimum via hole under the DSP/SDRAM, and is 3.3”x4” in dimensions. The board can be made smaller in the future by placing components on both sides.

ACKNOWLEDGEMENTS

This research was supported by the Open Prosthetics Project, specifically with generous donations from Douglas Abrams and William Becker. The work was indulged by Dr. Rob Clark at Duke University, and by the DARPA Revolutionizing Prosthetics Program, DARPA contract N66001-06-C8005, and by NSF grant DGE-0221632.

The first revision of the board is 6 layers, routed on 0.005” trace/space rules, with 0.006” minimum via hole under the DSP/SDRAM, and is 3.3”x4” in dimensions. The board can be made smaller in the future by placing components on both sides.

ACKNOWLEDGEMENTS

This research was supported by the Open Prosthetics Project, specifically with generous donations from Douglas Abrams and William Becker. The work was indulged by Dr. Rob Clark at Duke University, and by the DARPA Revolutionizing Prosthetics Program, DARPA contract N66001-06-C8005, and by NSF grant DGE-0221632.

REFERENCES

1. Feron, J., “New Process Will Help Amputee To Control Limb With Thought”, New York Times, August 16, 1965.

2. Carey, B. and Belfiore, M., “Bionic Made Better”, Popular Science Scitech (http://www.popsci.com/scitech/article/2007-08/bionic-made-better), August 22, 2007.

3. Adee, S., “A 'Manhattan Project' for the Next Generation of Bionic Arms,” IEEE Spectrum Online (http://www.spectrum.ieee.org/mar08/6069), March, 2008.

4. Schwartz, S.I. “Atomic Audit: The Costs and Consequences of U.S. Nuclear Weapons”, Washington, D.C., Brookings Institution Press, 1998.

5. Ezell, LN, "NASA Historical Data Book," Vol. II, NASA SP-4012, 1988, pp. 122-32.

6. Bolkcom, C. , "Joint Strike Fighter (JSF) Program: Background, Status, and Issues." Congressional Research Service Report: 12, 2002.

7. Department of Defense Fiscal Year (FY) 2005-2009 Budget Estimates, February 2006, February 2007, February 2008. Research, Development, Test And Evaluation, Defense-Wide. Volume 1 - Defense Advanced Research Projects Agency.

8. CNN Money, “Gillette unveils 5-bladed razor”, (http://money.cnn.com/2005/09/14/news/fortune500/gillette/), September 14, 2005.

9. Gilbert, S., “NPD December and 2007 Gaming Results: Incredible Video Game Sales”, Metue Media Entertainment and Technology (http://metue.com/01-17-2008/npd-december-2007-annual-videogame-sales/), January 17, 2008.

10. Smith, A., “Sex dysfunction drugs: Nowhere to grow?”, CNN Money (http://money.cnn.com/2006/01/05/news/companies/sexdysfunction/), January 5, 2006.

11. Dishneau, D., “War fuels prosthetics research blitz”, USA Today, July 16, 2007.

[^1] Feron, J., “New Process Will Help Amputee To Control Limb With Thought”, New York Times, August 16, 1965.
[^2] Carey, B. and Belfiore, M., “Bionic Made Better”, Popular Science Scitech (http://www.popsci.com/scitech/article/2007-08/bionic-made-better), August 22, 2007.
[^3] Adee, S., “A 'Manhattan Project' for the Next Generation of Bionic Arms,” IEEE Spectrum Online (http://www.spectrum.ieee.org/mar08/6069), March, 2008.
[^4] Schwartz, S.I. “Atomic Audit: The Costs and Consequences of U.S. Nuclear Weapons”,Washington, D.C., Brookings Institution Press, 1998.
[^5] Ezell, LN, "NASA Historical Data Book," Vol. II, NASA SP-4012, 1988, pp. 122-32.
[^6] Bolkcom, C. , "Joint Strike Fighter (JSF) Program: Background, Status, and Issues." Congressional Research Service Report: 12, 2002.
[^7] Department of Defense Fiscal Year (FY) 2005-2009 Budget Estimates, February 2006, February 2007, February 2008. Research, Development, Test and Evaluation, Defense-Wide. Volume 1 - Defense Advanced Research Projects Agency.
[^8] CNN Money, “Gillette unveils 5-bladed razor”, (http://money.cnn.com/2005/09/14/news/fortune500/gillette/), September 14, 2005.
[^9] Gilbert, S., “NPD December and 2007 Gaming Results: Incredible Video Game Sales”, Metue Media Entertainment and Technology (http://metue.com/01-17-2008/npd-december-2007-annual-video-game-sales/), January 17, 2008.
[^10] Smith, A., “Sex dysfunction drugs: Nowhere to grow?”, CNN Money (http://money.cnn.com/2006/01/05/news/companies/sexdysfunction/), January 5, 2006.
[^11] Dishneau, D., “War fuels prosthetics research blitz”, USA Today, July 16, 2007.

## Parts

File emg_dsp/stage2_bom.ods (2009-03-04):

value | footprint | DIGIKEY PN | SPLYR | order count | board count | references
ADG726 | LFCSP-48 |  | adi | 1 | 1 | U24
25 | 402 | RHM27JCT-ND (http://search.digikey.com/scripts/DkSearch/dksus.dll?Detail&name=RHM27JCT-ND) | d | 10 | 3 | R16 R14 R13
33 | 402 | P33JCT-ND (http://search.digikey.com/scripts/DkSearch/dksus.dll?Detail&name=P33JCT-ND) | d | 10 | 7 | R3 R4 R1 R22 R23 R24 R25
0.001uf | 402 | PCC1721CT-ND (http://search.digikey.com/scripts/DkSearch/dksus.dll?Detail&name=PCC1721CT-ND) | d | 10 | 9 | C40 C11 C14 C8 C26 C27 C25 C142 C141
0.012uf | 402 | PCC1700CT-ND (http://search.digikey.com/scripts/DkSearch/dksus.dll?Detail&name=PCC1700CT-ND) | d | 10 | 5 | C65 C66 C57 C58 C56
0.01uf | 402 | 490-4516-1-ND (http://search.digikey.com/scripts/DkSearch/dksus.dll?Detail&name=490-4516-1-ND) | d | 20 | 12 | C126 C127 C137 C138 C42 C16 C18 C29 C31 C36 C38 C5
0.047uf | 402 | PCC2142CT-ND (http://search.digikey.com/scripts/DkSearch/dksus.dll?Detail&name=PCC2142CT-ND) | d | 40 | 32 | C87 C88 C89 C90 C91 C92 C93 C94 C95 C96 C97 C98 C99 C100 C101 C102 C103 C104 C105 C106 C107 C108 C109 C110 C111 C112 C113 C114 C115 C116 C117 C118
0.1uf | 402 | 399-3520-1-ND (http://search.digikey.com/scripts/DkSearch/dksus.dll?Detail&name=399-3520-1-ND) | d | 20 | 15 | C59 C60 C85 C86 C83 C6 C39 C41 C2 C45 C7 C10 C3 C4 C144
1.5pF | 402 | 311-1003-1-ND (http://search.digikey.com/scripts/DkSearch/dksus.dll?Detail&name=311-1003-1-ND) | d | 10 | 1 | C44
10k | 402 | RHM10.0KLCT-ND (http://search.digikey.com/scripts/DkSearch/dksus.dll?Detail&name=RHM10.0KLCT-ND) | d | 10 | 7 | R17 R18 R20 R21 R9 R11 R12
12.5k | 402 | P12.4KLCT-ND (http://search.digikey.com/scripts/DkSearch/dksus.dll?Detail&name=P12.4KLCT-ND) | d | 10 | 4 | R45 R46 R61 R62
1pF | 402 | 587-1007-1-ND (http://search.digikey.com/scripts/DkSearch/dksus.dll?Detail&name=587-1007-1-ND) | d | 10 | 1 | C47
1uf | 402 | 490-1319-1-ND (http://search.digikey.com/scripts/DkSearch/dksus.dll?Detail&name=490-1319-1-ND) | d | 30 | 22 | C119 C121 C120 C122 C123 C128 C129 C130 C132 C131 C133 C134 C139 C140 C46 C19 C21 C32 C33 C35 C15 C12
2.2k | 402 | RHM2.2KJCT-ND (http://search.digikey.com/scripts/DkSearch/dksus.dll?Detail&name=RHM2.2KJCT-ND) | d | 10 | 8 | R26 R27 R28 R29 R30 R31 R32 R33
2.2nF | 402 | PCC222BQCT-ND (http://search.digikey.com/scripts/DkSearch/dksus.dll?Detail&name=PCC222BQCT-ND) | d | 2 | 1 | C48
2.2uf | 402 | PCC2421CT-ND (http://search.digikey.com/scripts/DkSearch/dksus.dll?Detail&name=PCC2421CT-ND) | d | 20 | 11 | C64 C63 C54 C61 C62 C55 C53 C49 C50 C51 C52
2.7nH | 402 | PCD1851CT-ND (http://search.digikey.com/scripts/DkSearch/dksus.dll?Detail&name=PCD1851CT-ND) | d | 2 | 1 | L5
20k | 402 | RHM20.0KLCT-ND (http://search.digikey.com/scripts/DkSearch/dksus.dll?Detail&name=RHM20.0KLCT-ND) | d | 10 | 4 | R47 R48 R63 R64
220k | 402 | RHM220KJCT-ND (http://search.digikey.com/scripts/DkSearch/dksus.dll?Detail&name=RHM220KJCT-ND) | d | 10 | 1 | R5
22K | 402 | P22.0KLCT-ND (http://search.digikey.com/scripts/DkSearch/dksus.dll?Detail&name=P22.0KLCT-ND) | d | 10 | 1 | R19
270k | 402 | RHM270KJCT-ND (http://search.digikey.com/scripts/DkSearch/dksus.dll?Detail&name=RHM270KJCT-ND) | d | 10 | 1 | R8
3.3k | 402 | RHM3.30KLCT-ND (http://search.digikey.com/scripts/DkSearch/dksus.dll?Detail&name=RHM3.30KLCT-ND) | d | 10 | 4 | R36 R37 R39 R40
3.9nH | 402 | PCD1853CT-ND (http://search.digikey.com/scripts/DkSearch/dksus.dll?Detail&name=PCD1853CT-ND) | d | 2 | 1 | L4
327k | 402 | P324KLCT-ND (http://search.digikey.com/scripts/DkSearch/dksus.dll?Detail&name=P324KLCT-ND) | d | 10 | 4 | R34 R35 R41 R42
33k | 402 | P33.0KLCT-ND (http://search.digikey.com/scripts/DkSearch/dksus.dll?Detail&name=P33.0KLCT-ND) | d | 10 | 4 | R49 R50 R65 R66
33nF | 402 | PCC2140CT-ND (http://search.digikey.com/scripts/DkSearch/dksus.dll?Detail&name=PCC2140CT-ND) | d | 2 | 1 | C37
33pf | 402 | 490-3220-1-ND (http://search.digikey.com/scripts/DkSearch/dksus.dll?Detail&name=490-3220-1-ND) | d | 10 | 1 | C20
3k | 402 | 541-3.00KLCT-ND (http://search.digikey.com/scripts/DkSearch/dksus.dll?Detail&name=541-3.00KLCT-ND) | d | 10 | 4 | R43 R44 R59 R60
4.7pF | 402 | 587-1023-1-ND (http://search.digikey.com/scripts/DkSearch/dksus.dll?Detail&name=587-1023-1-ND) | d | 10 | 1 | C43
47k | 402 | RHM47.0KLCT-ND (http://search.digikey.com/scripts/DkSearch/dksus.dll?Detail&name=RHM47.0KLCT-ND) | d | 10 | 4 | R51 R52 R67 R68
50k | 402 | RHM49.9KLCT-ND (http://search.digikey.com/scripts/DkSearch/dksus.dll?Detail&name=RHM49.9KLCT-ND) | d | 10 | 2 | R15 R10
5pf | 402 | 311-1010-1-ND (http://search.digikey.com/scripts/DkSearch/dksus.dll?Detail&name=311-1010-1-ND) | d | 10 | 1 | C30
6.5k | 402 | P6.49KLCT-ND (http://search.digikey.com/scripts/DkSearch/dksus.dll?Detail&name=P6.49KLCT-ND) | d | 10 | 4 | R55 R56 R71 R72
68nf | 402 | PCC2144CT-ND (http://search.digikey.com/scripts/DkSearch/dksus.dll?Detail&name=PCC2144CT-ND) | d | 10 | 4 | C124 C125 C135 C136
7pf | 402 | 490-1277-1-ND (http://search.digikey.com/scripts/DkSearch/dksus.dll?Detail&name=490-1277-1-ND) | d | 10 | 1 | C28
8.2nH | 402 | PCD1857CT-ND (http://search.digikey.com/scripts/DkSearch/dksus.dll?Detail&name=PCD1857CT-ND) | d | 2 | 1 | L3
825k | 402 | P825KLCT-ND (http://search.digikey.com/scripts/DkSearch/dksus.dll?Detail&name=P825KLCT-ND) | d | 10 | 1 | R6
8pf | 402 | PCC080CQCT-ND (http://search.digikey.com/scripts/DkSearch/dksus.dll?Detail&name=PCC080CQCT-ND) | d | 10 | 2 | C13 C17
9.2k | 402 | RHM9.10KLCT-ND (http://search.digikey.com/scripts/DkSearch/dksus.dll?Detail&name=RHM9.10KLCT-ND) | d | 10 | 4 | R53 R54 R69 R70
90k | 402 | RHM90.9KLCT-ND (http://search.digikey.com/scripts/DkSearch/dksus.dll?Detail&name=RHM90.9KLCT-ND) | d | 10 | 1 | R7
ferrite | 402 | 587-1843-1-ND (http://search.digikey.com/scripts/DkSearch/dksus.dll?Detail&name=587-1843-1-ND) | d | 10 | 1 | L6
0.1uf | 603 | 399-1283-1-ND (http://search.digikey.com/scripts/DkSearch/dksus.dll?Detail&name=399-1283-1-ND) | d | 10 | 1 | C71
10uf | 603 | PCC2395CT-ND (http://search.digikey.com/scripts/DkSearch/dksus.dll?Detail&name=PCC2395CT-ND) | d | 8 | 6 | C22 C23 C9 C24 C34 C1
1uf | 603 | 587-1241-1-ND (http://search.digikey.com/scripts/DkSearch/dksus.dll?Detail&name=587-1241-1-ND) | d | 20 | 7 | C73 C70 C69 C68 C67 C77 C79
3.3k | 603 | RHM3.3KGCT-ND (http://search.digikey.com/scripts/DkSearch/dksus.dll?Detail&name=RHM3.3KGCT-ND) | d | 10 | 1 | R38
4.7uf | 603 | 490-3302-1-ND (http://search.digikey.com/scripts/DkSearch/dksus.dll?Detail&name=490-3302-1-ND) | d | 10 | 9 | C75 C76 C80 C81 C74 C82 C84 C78 C143
INDUCTOR | 603 | 445-1553-1-ND (http://search.digikey.com/scripts/DkSearch/dksus.dll?Detail&name=445-1553-1-ND) | d | 10 | 2 | L7 L8
LED | 603 | 754-1357-1-ND (http://search.digikey.com/scripts/DkSearch/dksus.dll?Detail&name=754-1357-1-ND) | d | 4 | 4 | D4 D5 D6 D7
2.2uh | 805 | 490-4994-1-ND (http://search.digikey.com/scripts/DkSearch/dksus.dll?Detail&name=490-4994-1-ND) | d | 2 | 2 | L1 L2
150uf | 2x100mil | 565-3048-ND (http://search.digikey.com/scripts/DkSearch/dksus.dll?Detail&name=565-3048-ND) | d | 1 | 1 | C145
JUMP | 2x100mil | WM8072-ND (http://search.digikey.com/scripts/DkSearch/dksus.dll?Detail&name=WM8072-ND) | d | 10 | 8 | U25 U40 U33 U2 U10 U11 U1 U13
8X2X100 | 2x8x100mil | 609-3238-ND (http://search.digikey.com/scripts/DkSearch/dksus.dll?Detail&name=609-3238-ND) | d | 2 | 2 | U32 U23
ADSP_JTAG_CON | 7x2x100 | A26529-07-ND (http://search.digikey.com/scripts/DkSearch/dksus.dll?Detail&name=A26529-07-ND) | d | 1 | 1 | U12
8X100 | 8x100mil | 609-3273-ND (http://search.digikey.com/scripts/DkSearch/dksus.dll?Detail&name=609-3273-ND) | d | 3 | 1 | U43
RS232_CON | DB9 | A32115-ND (http://search.digikey.com/scripts/DkSearch/dksus.dll?Detail&name=A32115-ND) | d | 1 | 1 | U8
FCI_USB_B | FCI_USB_B | 609-1039-ND (http://search.digikey.com/scripts/DkSearch/dksus.dll?Detail&name=609-1039-ND) | d | 1 | 1 | U147
BF532-160 | MBGA-160 | ADSP-BF532SBBCZ400-ND (http://search.digikey.com/scripts/DkSearch/dksus.dll?Detail&name=ADSP-BF532SBBCZ400-ND) | d | 1 | 1 | U15
LMV1032-15 | MicroSMD-4 | LMV1032UP-15CT-ND (http://search.digikey.com/scripts/DkSearch/dksus.dll?Detail&name=LMV1032UP-15CT-ND) | d | 40 | 32
LMV1032-25 | microSMD-4 | LMV1032UP-25CT-ND (http://search.digikey.com/scripts/DkSearch/dksus.dll?Detail&name=LMV1032UP-25CT-ND) | d | 70 | 64 | U47 U48 U49 U50 U51 U52 U53 U54 U55 U56 U57 U58 U59 U60 U61 U62 U63 U64 U65 U66 U67 U68 U69 U70 U71 U72 U73 U74 U75 U76 U77 U78 U79 U80 U81 U82 U83 U84 U85 U86 U87 U88 U89 U90 U91 U92 U93 U94 U95 U96 U97 U98 U99 U100 U101 U102 U103 U104 U105 U106 U107 U108 U109 U110 U111 U112 U113 U114 U115 U116 U117 U118 U119 U120 U121 U122 U123 U124 U125 U126 U127 U128 U129 U130 U131 U132 U133 U134 U135 U136 U137 U138 U139 U140 U141 U142
NX3225SA | NDK_XTAL | 644-1047-1-ND (http://search.digikey.com/scripts/DkSearch/dksus.dll?Detail&name=644-1047-1-ND) | d | 1 | 1 | U5
TPS62410 | QFN-10 | 296-21647-1-ND (http://search.digikey.com/scripts/DkSearch/dksus.dll?Detail&name=296-21647-1-ND) | d | 1 | 1 | U6
ISL28470 | QSOP-28 | ISL28470FAZ-ND (http://search.digikey.com/scripts/DkSearch/dksus.dll?Detail&name=ISL28470FAZ-ND) | d | 1 | 1 | U41
MAX6711 | SC-70-4 | MAX6711REXS+TCT-ND (http://search.digikey.com/scripts/DkSearch/dksus.dll?Detail&name=MAX6711REXS%2BTCT-ND) | d | 1 | 1 | U20
TPS71727 | SC-70-5 | 296-19648-1-ND (http://search.digikey.com/scripts/DkSearch/dksus.dll?Detail&name=296-19648-1-ND) | d | 2 | 2 | U26 U27
UCLAMP33 | SOD-323 | UCLAMP3301HCT-ND (http://search.digikey.com/scripts/DkSearch/dksus.dll?Detail&name=UCLAMP3301HCT-ND) | d | 2 | 2 | D8 D9
uclamp0501 | SOD-523 | UCLAMP0501HCT-ND (http://search.digikey.com/scripts/DkSearch/dksus.dll?Detail&name=UCLAMP0501HCT-ND) | d | 4 | 3 | D3 D2 D1
MCP3304 | SOIC-16 | MCP3304-CI/SL-ND (http://search.digikey.com/scripts/DkSearch/dksus.dll?Detail&name=MCP3304-CI/SL-ND) | d | 1 | 1 | U42
AT45DB081D | SOIC-8 | AT45DB081D-SSU-ND (http://search.digikey.com/scripts/DkSearch/dksus.dll?Detail&name=AT45DB081D-SSU-ND) | d | 1 | 1 | U18
REG101 | SOIC-8 | REG101UA-5-ND (http://search.digikey.com/scripts/DkSearch/dksus.dll?Detail&name=REG101UA-5-ND) | d | 1 | 1 | U39
TLE2426 | SOIC-8 | 296-1345-1-ND (http://search.digikey.com/scripts/DkSearch/dksus.dll?Detail&name=296-1345-1-ND) | d | 1 | 1 | U38
ADUM2400 | SOICW-16 | ADUM2400BRWZ-ND (http://search.digikey.com/scripts/DkSearch/dksus.dll?Detail&name=ADUM2400BRWZ-ND) | d | 2 | 2 | U46 U45
BAT54A | SOT-23 | BAT54A-FDICT-ND (http://search.digikey.com/scripts/DkSearch/dksus.dll?Detail&name=BAT54A-FDICT-ND) | d | 1 | 1 | U9
ZR4040-2.5 | SOT-23 | ZR40401F25CT-ND (http://search.digikey.com/scripts/DkSearch/dksus.dll?Detail&name=ZR40401F25CT-ND) | d | 1 | 1 | U44
THS4281 | SOT-23-5 | 296-17000-1-ND (http://search.digikey.com/scripts/DkSearch/dksus.dll?Detail&name=296-17000-1-ND) | d | 2 | 2 | U29 U28
ADCS7476 | SOT-23-6 | ADCS7476AIMFCT-ND (http://search.digikey.com/scripts/DkSearch/dksus.dll?Detail&name=ADCS7476AIMFCT-ND) | d | 2 | 2 | U31 U30
BAV199 | SOT-363 | BAV199DW-FDICT-ND (http://search.digikey.com/scripts/DkSearch/dksus.dll?Detail&name=BAV199DW-FDICT-ND) | d | 5 | 4 | U34 U35 U36 U37
MAX3421E | TQFP-32 | MAX3421EETJ+-ND (http://search.digikey.com/scripts/DkSearch/dksus.dll?Detail&name=MAX3421EETJ%2B-ND) | d | 1 | 1 | U3
OPA4348 | TSSOP-14 | 296-12278-1-ND (http://search.digikey.com/scripts/DkSearch/dksus.dll?Detail&name=296-12278-1-ND) | d | 2 | 2 | U143 U144
ADM3202 | TSSOP-16 | ADM3202ARUZ-ND (http://search.digikey.com/scripts/DkSearch/dksus.dll?Detail&name=ADM3202ARUZ-ND) | d | 1 | 1 | U4
74LCX541 | TSSOP-20 | MC74LCX541DTR2GOSCT-ND (http://search.digikey.com/scripts/DkSearch/dksus.dll?Detail&name=MC74LCX541DTR2GOSCT-ND) | d | 2 | 2 | U19 U22
OMNETICS_36 | omnetics_36 | gary | g | 1 | 1 | U145
THS4281 | SOT23-5 | 595-THS4281DBVT | m | 2
ABM10XTAL | ABM10 | 815-ABM10-16-E20-T (http://mouser.com/Search/ProductDetail.aspx?qs=sGAEpiMZZMtg8rPr%252bGIKJkxOrMeUzlBhHDemd1yVNGM%3D) | m | 1 | 1 | U14
ANTENNA | chip_ant |  | sfe |  | 1 | U146
NRF24L01 | QFN-20 |  | sfe |  | 1 | U17
100k | 402 | RHM100KJCT-ND (http://search.digikey.com/scripts/DkSearch/dksus.dll?Detail&name=RHM100KJCT-ND) |  | 10 | 1 | R2
22k | 402 | see 22K above |  |  | 4 | R57 R58 R73 R74
10nf | 603 | use 12nf below |  |  | 1 | C72
VAL** | 2.9mm_hole | na |  |  | 5 | 2.9mm_hole 2.9mm_hole 2.9mm_hole 2.9mm_hole 2.9mm_hole
TESTCON | 7x100mil | see 8x100 below |  |  | 2 | U21 U16
TP | TP | na |  |  | 12 | TP1 TP2 TP4 TP3 TP5 TP6 TP7 TP8 TP10 TP9 TP11 TP12

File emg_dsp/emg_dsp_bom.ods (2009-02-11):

value | footprint | supplier | pn | count | note | references
OPA4348 | TSSOP-14 | Digi-key | 296-12277-5-ND (http://search.digikey.com/scripts/DkSearch/dksus.dll?Detail?name=296-12277-5-ND) | 8 |  | U105 U99 U93 U87 U81 U75 U69 U63
TLE2426 | SOIC-8 | Digi-key | 296-1345-5-ND (http://search.digikey.com/scripts/DkSearch/dksus.dll?Detail?name=296-1345-5-ND) | 1 |  | U109
74LV594ADBR | TSSOP-16 | Digi-key | 296-3843-1-ND (http://search.digikey.com/scripts/DkSearch/dksus.dll?Detail?name=296-3843-1-ND) | 1 | 595 not 594? | U3
180 | 402 | Digi-key | 311-180JRCT-ND (http://search.digikey.com/scripts/DkSearch/dksus.dll?Detail?name=311-180JRCT-ND) | 2 |  | R25 R22
0.001uf | 402 | Digi-key | 399-1032-1-ND (http://search.digikey.com/scripts/DkSearch/dksus.dll?Detail?name=399-1032-1-ND) | 2 |  | C51 C38
0.022uf | 402 | Digi-key | 399-3015-1-ND (http://search.digikey.com/scripts/DkSearch/dksus.dll?Detail?name=399-3015-1-ND) | 1 |  | C23
0.1uf | 402 | Digi-key | 399-3027-1-ND (http://search.digikey.com/scripts/DkSearch/dksus.dll?Detail?name=399-3027-1-ND) | 48 |  | C202 C203 C189 C190 C176 C177 C163 C164 C150 C151 C137 C138 C124 C125 C111 C112 C87 C89 C83 C4 C10 C41 C61 C16 C28 C29 C26 C24 C15 C45 C46 C47 C48 C49 C52 C53 C33 C34 C35 C11 C9 C7 C6 C5 C8 C72 C209 C215
3.3uh | 1210 | Digi-key | 445-1537-1-ND (http://search.digikey.com/scripts/DkSearch/dksus.dll?Detail?name=445-1537-1-ND) | 2 | 700ma | L1 L3
ferrite | 603 | Digi-key | 445-1547-1-ND (http://search.digikey.com/scripts/DkSearch/dksus.dll?Detail?name=445-1547-1-ND) | 3 |  | L4 L2 L7
10uf_tant | 805 | Digi-key | 511-1447-1-ND (http://search.digikey.com/scripts/DkSearch/dksus.dll?Detail?name=511-1447-1-ND) | 2 | 6.3V | C90 C92
ABM10XTAL | ABM10 | Digi-key | 535-9095-1-ND (http://search.digikey.com/scripts/DkSearch/dksus.dll?Detail?name=535-9095-1-ND) | 1 | 25Mhz | U21
25 | 402 | Digi-key | 541-24JCT-ND (http://search.digikey.com/scripts/DkSearch/dksus.dll?Detail?name=541-24JCT-ND) | 4 |  | R11 R9 R190 R189
4.5k | 402 | Digi-key | 541-4.53KLCT-ND (http://search.digikey.com/scripts/DkSearch/dksus.dll?Detail?name=541-4.53KLCT-ND) | 16 |  | R182 R183 R166 R167 R150 R151 R134 R135 R118 R119 R102 R103 R86 R87 R70 R71
5k | 402 | Digi-key | 541-4.99KLCT-ND (http://search.digikey.com/scripts/DkSearch/dksus.dll?Detail?name=541-4.99KLCT-ND) | 1 |  | R18
5.6k | 402 | Digi-key | 541-5.60KLCT-ND (http://search.digikey.com/scripts/DkSearch/dksus.dll?Detail?name=541-5.60KLCT-ND) | 16 |  | R180 R181 R164 R165 R148 R149 R132 R133 R116 R117 R100 R101 R84 R85 R68 R69
50k | 402 | Digi-key | 541-51KJCT-ND (http://search.digikey.com/scripts/DkSearch/dksus.dll?Detail?name=541-51KJCT-ND) | 4 |  | R7 R23 R42 R51
56.2 | 402 | Digi-key | 541-56.2LCT-ND (http://search.digikey.com/scripts/DkSearch/dksus.dll?Detail?name=541-56.2LCT-ND) | 1 |  | R188
58k | 402 | Digi-key | 541-57.6KLCT-ND (http://search.digikey.com/scripts/DkSearch/dksus.dll?Detail?name=541-57.6KLCT-ND) | 16 |  | R172 R173 R156 R157 R140 R141 R124 R125 R108 R109 R92 R93 R76 R77 R60 R61
820k | 402 | Digi-key | 541-820KLCT-ND (http://search.digikey.com/scripts/DkSearch/dksus.dll?Detail?name=541-820KLCT-ND) | 16 |  | R178 R179 R162 R163 R146 R147 R130 R131 R114 R115 R98 R99 R82 R83 R66 R67
MT48LC16M16A2 | VFBGA-54 | Digi-key | 557-1190-1-ND (http://search.digikey.com/scripts/DkSearch/dksus.dll?Detail?name=557-1190-1-ND) | 1 |  | U10
BC847BPN | SOT-363 | Digi-key | 568-1634-1-ND (http://search.digikey.com/scripts/DkSearch/dksus.dll?Detail?name=568-1634-1-ND) | 32 |  | U100 U101 U102 U103 U94 U95 U96 U97 U88 U89 U90 U91 U82 U83 U84 U85 U76 U77 U78 U79 U70 U71 U72 U73 U64 U65 U66 U67 U58 U59 U60 U61
78250M | 78250 | mouser | 580-78250MVC (http://www.mouser.com/Search/ProductDetail.aspx?qs=Sp7jPs%2FGXrMRMYRzP2NweA%3D%3D) | 1 |  | U46
FCI_USB_B | FCI_USB_A | Digi-key | 609-1039-ND | 1 |  | U35
LAN83C185 | TQFP-64 | Digi-key | 638-1009-ND | 1 |  | U15
ZENER | 603 | Digi-key | 641-1031-1-ND (http://search.digikey.com/scripts/DkSearch/dksus.dll?Detail?name=641-1031-1-ND) | 1 | 150mw | D12
NX3225SA | NDK_XTAL | Digi-key | 644-1047-1-ND (http://search.digikey.com/scripts/DkSearch/dksus.dll?Detail?name=644-1047-1-ND) | 1 | 12Mhz | U106
S8354MC | SOT-23-5 | Digi-key | 728-1036-1-ND (http://search.digikey.com/scripts/DkSearch/dksus.dll?Detail?name=728-1036-1-ND) | 1 |  | U27 | S-8354A50MC-JRJT2G
74LCX541 | TSSOP-20 | Digi-key | 74LCX541MTCXCT-ND (http://search.digikey.com/scripts/DkSearch/dksus.dll?Detail?name=74LCX541MTCXCT-ND) | 3 |  | U22 U18 U4
LED | 603 | Digi-key | 754-1123-1-ND (http://search.digikey.com/scripts/DkSearch/dksus.dll?Detail?name=754-1123-1-ND) | 2 | red | D5 D6
0.47uf | 402 | mouser | 81-GRM155F51A474ZE01 (http://www.mouser.com/Search/ProductDetail.aspx?qs=ACKugjZjxqm4nsyUXE3ktQ%3D%3D) | 32 |  | C196 C198 C197 C199 C183 C185 C184 C186 C170 C172 C171 C173 C157 C159 C158 C160 C144 C146 C145 C147 C131 C133 C132 C134 C118 C120 C119 C121 C105 C107 C106 C108
0.15uf | 402 | mouser | 81-GRM155R61A154KE9D (http://www.mouser.com/Search/ProductDetail.aspx?qs=9U7yHM2lsjT7dQhtoCVLBg%3D%3D) | 16 |  | C200 C201 C187 C188 C174 C175 C161 C162 C148 C149 C135 C136 C122 C123 C109 C110
6.8nf | 402 | mouser | 81-GRM155R71E682JA1D (http://www.mouser.com/Search/ProductDetail.aspx?qs=c4yvaafl%252bAxa5cLq%2FC0Kkw%3D%3D) | 2 |  | C19 C20
TESTCON | 7x100mil | Digi-key | A19434-ND (http://search.digikey.com/scripts/DkSearch/dksus.dll?Detail?name=A19434-ND) | 1 |  | U1
8X2X100 | 2x8x100mil | Digi-key | A33163-ND (http://search.digikey.com/scripts/DkSearch/dksus.dll?Detail?name=A33163-ND) | 2 | shrouded | U36 U37
RS232_CON | DB9 | Digi-key | A35114-ND | 1 |  | U14
ADM3202 | TSSOP-16 | Digi-key | ADM3202ARUZ-ND (http://search.digikey.com/scripts/DkSearch/dksus.dll?Detail?name=ADM3202ARUZ-ND) | 1 |  | U12
ADM6713 | SC-70-4 | Digi-key | ADM6713SAKSZ-REEL7CT-ND (http://search.digikey.com/scripts/DkSearch/dksus.dll?Detail?name=ADM6713SAKSZ-REEL7CT-ND) | 1 |  | U7
BF534/6/7 | MBGA-182 | Digi-key | ADSP-BF537KBCZ-6AV-ND (http://search.digikey.com/scripts/DkSearch/dksus.dll?Detail?name=ADSP-BF537KBCZ-6AV-ND) | 1 | 600mhz hipow | U16
ADUM2400 | SOICW-16 | Digi-key | ADUM2400BRWZ-ND (http://search.digikey.com/scripts/DkSearch/dksus.dll?Detail?name=ADUM2400BRWZ-ND) | 2 | 10mbps | U39 U40
ADSP_JTAG_CON | 7x2x100 | Digi-key | AHS14L-ND (http://search.digikey.com/scripts/DkSearch/dksus.dll?Detail?name=AHS14L-ND) | 1 |  | U19
AT45DB081D | SOIC-8 | Digi-key | AT45DB081D-SSU-ND (http://search.digikey.com/scripts/DkSearch/dksus.dll?Detail?name=AT45DB081D-SSU-ND) | 1 |  | U8
BAT54A | SOT-23 | Digi-key | BAT54ATPMSCT-ND (http://search.digikey.com/scripts/DkSearch/dksus.dll?Detail?name=BAT54ATPMSCT-ND) | 4 |  | U31 U26 U32 U108
BAT54S | SOT-23 | Digi-key | BAT54SCT-ND (http://search.digikey.com/scripts/DkSearch/dksus.dll?Detail?name=BAT54SCT-ND) | 4 |  | U45 U48 U23 U24
CAT32TDI | SOT-23-6 | Digi-key | CAT32TDI-TE7CT-ND (http://search.digikey.com/scripts/DkSearch/dksus.dll?Detail?name=CAT32TDI-TE7CT-ND) | 1 |  | U28
F2110 | 1206 | Digi-key | F2110CT-ND (http://search.digikey.com/scripts/DkSearch/dksus.dll?Detail?name=F2110CT-ND) | 1 |  | F1
FAN2001 | MLP-6 | Digi-key | FAN2001MPXCT-ND (http://search.digikey.com/scripts/DkSearch/dksus.dll?Detail?name=FAN2001MPXCT-ND) | 2 |  | U5 U11
FDV301N | SOT-23 | Digi-key | FDV301NCT-ND | 1 |  | U13
INA2322 | TSSOP-14 | Digi-key | INA2322EACT-ND (http://search.digikey.com/scripts/DkSearch/dksus.dll?Detail?name=INA2322EACT-ND) | 8 |  | U104 U98 U92 U86 U80 U74 U68 U62
MAX253 | SOIC-8 | Digi-key | MAX253CSA+-ND (http://search.digikey.com/scripts/DkSearch/dksus.dll?Detail?name=MAX253CSA%2B-ND) | 1 | comm. Temp. | U47
MAX3421E | TQFP-32 | Digi-key | MAX3421EEHJ+-ND (http://search.digikey.com/scripts/DkSearch/dksus.dll?Detail?name=MAX3421EEHJ%2B-ND) | 1 |  | U29
MCP3304 | SOIC-16 | Digi-key | MCP3304-CI/SL-ND (http://search.digikey.com/scripts/DkSearch/dksus.dll?Detail?name=MCP3304-CI%2FSL-ND) | 4 |  | U57 U55 U53 U51
MNR18 | 0603x8 | Digi-key | MNR18222CT-ND (http://search.digikey.com/scripts/DkSearch/dksus.dll?Detail?name=MNR18222CT-ND) | 4 | 2.2k | U56 U54 U52 U50
NDS336P | SOT-23 | Digi-key | NDS336PCT-ND (http://search.digikey.com/scripts/DkSearch/dksus.dll?Detail?name=NDS336PCT-ND) | 2 |  | Q2 Q3
NDDS336P | SOT-23 | Digi-key | NDS336PCT-ND (http://search.digikey.com/scripts/DkSearch/dksus.dll?Detail?name=NDS336PCT-ND) | 1 |  | Q1
12.4k | 603 | Digi-key | P12.4KHCT-ND (http://search.digikey.com/scripts/DkSearch/dksus.dll?Detail?name=P12.4KHCT-ND) | 1 |  | R20
100uf | 2mmradial | Digi-key | P13455-ND (http://search.digikey.com/scripts/DkSearch/dksus.dll?Detail?name=P13455-ND) | 5 |  | C88 C1 C75 C68 C77
2.2k | 402 | Digi-key | P2.2KJCT-ND (http://search.digikey.com/scripts/DkSearch/dksus.dll?Detail?name=P2.2KJCT-ND) | 2 |  | R37 R40
500k | 402 | Digi-key | P510KJCT-ND (http://search.digikey.com/scripts/DkSearch/dksus.dll?Detail?name=P510KJCT-ND) | 5 |  | R24 R38 R46 R53 R191
7pf | 402 | Digi-key | PCC070CQCT-ND (http://search.digikey.com/scripts/DkSearch/dksus.dll?Detail?name=PCC070CQCT-ND) | 2 |  | C67 C70
0.01uf | 402 | Digi-key | PCC103BQCT-ND (http://search.digikey.com/scripts/DkSearch/dksus.dll?Detail?name=PCC103BQCT-ND) | 27 |  | C204 C205 C191 C192 C178 C179 C165 C166 C152 C153 C139 C140 C126 C127 C113 C114 C85 C22 C62 C60 C40 C43 C55 C59 C54 C37 C39
18pf | 402 | Digi-key | PCC180CQCT-ND (http://search.digikey.com/scripts/DkSearch/dksus.dll?Detail?name=PCC180CQCT-ND) | 2 |  | C80 C82
10uf | 805 | Digi-key | PCC2182CT-ND (http://search.digikey.com/scripts/DkSearch/dksus.dll?Detail?name=PCC2182CT-ND) | 6 |  | C42 C63 C14 C76 C213 C214
2nf | 402 | Digi-key | PCC223FQCT-ND (http://search.digikey.com/scripts/DkSearch/dksus.dll?Detail?name=PCC223FQCT-ND) | 4 |  | C31 C64 C18 C74
1uf | 402 | Digi-key | PCC2268CT-ND (http://search.digikey.com/scripts/DkSearch/dksus.dll?Detail?name=PCC2268CT-ND) | 57 |  | C206 C208 C207 C193 C195 C194 C102 C104 C103 C180 C182 C181 C167 C169 C168 C99 C101 C100 C154 C156 C155 C141 C143 C142 C96 C98 C97 C128 C130 C129 C115 C117 C116 C93 C95 C94 C84 C91 C86 C25 C21 C57 C79 C2 C17 C73 C69 C78 C58 C65 C66 C71 C56 C81 C212 C210 C211
10uf | 603 | Digi-key | PCC2367CT-ND (http://search.digikey.com/scripts/DkSearch/dksus.dll?Detail?name=PCC2367CT-ND) | 9 |  | C44 C50 C32 C36 C3 C12 C13 C27 C30
6.8uh | 1008 | Digi-key | PCD1238CT-ND (http://search.digikey.com/scripts/DkSearch/dksus.dll?Detail?name=PCD1238CT-ND) | 1 |  | L6
33uh | ELL6 | Digi-key | PCD1710CT-ND (http://search.digikey.com/scripts/DkSearch/dksus.dll?Detail?name=PCD1710CT-ND) | 1 | 500ma | L5
REG101 | SOIC-8 | Digi-key | REG101UA-5-ND (http://search.digikey.com/scripts/DkSearch/dksus.dll?Detail?name=REG101UA-5-ND) | 1 |  | U107
1.5k | 402 | Digi-key | RHM1.5KJCT-ND (http://search.digikey.com/scripts/DkSearch/dksus.dll?Detail?name=RHM1.5KJCT-ND) | 2 |  | R31 R186
10k | 402 | Digi-key | RHM10.0KLCT-ND (http://search.digikey.com/scripts/DkSearch/dksus.dll?Detail?name=RHM10.0KLCT-ND) | 32 |  | R170 R171 R154 R155 R138 R139 R122 R123 R106 R107 R90 R91 R74 R75 R58 R59 R4 R1 R6 R5 R21 R26 R28 R30 R29 R27 R36 R39 R43 R41 R19 R187
100k | 402 | Digi-key | RHM100KLCT-ND (http://search.digikey.com/scripts/DkSearch/dksus.dll?Detail?name=RHM100KLCT-ND) | 21 |  | R176 R177 R160 R161 R144 R145 R128 R129 R112 R113 R96 R97 R80 R81 R64 R65 R35 R2 R54 R44 R13
10 | 402 | Digi-key | RHM10JCT-ND (http://search.digikey.com/scripts/DkSearch/dksus.dll?Detail?name=RHM10JCT-ND) | 1 |  | R14
180k | 402 | Digi-key | RHM180KJCT-ND (http://search.digikey.com/scripts/DkSearch/dksus.dll?Detail?name=RHM180KJCT-ND) | 2 |  | R33 R47
22k | 402 | Digi-key | RHM22.0KLCT-ND (http://search.digikey.com/scripts/DkSearch/dksus.dll?Detail?name=RHM22.0KLCT-ND) | 16 |  | R184 R185 R168 R169 R152 R153 R136 R137 R120 R121 R104 R105 R88 R89 R72 R73
270 | 402 | Digi-key | RHM270JCT-ND (http://search.digikey.com/scripts/DkSearch/dksus.dll?Detail?name=RHM270JCT-ND) | 2 |  | R8 R10
3.3k | 402 | Digi-key | RHM3.30KLCT-ND (http://search.digikey.com/scripts/DkSearch/dksus.dll?Detail?name=RHM3.30KLCT-ND) | 17 |  | R174 R175 R158 R159 R142 R143 R126 R127 R110 R111 R94 R95 R78 R79 R62 R63 R57
30k | 402 | Digi-key | RHM30KJCT-ND (http://search.digikey.com/scripts/DkSearch/dksus.dll?Detail?name=RHM30KJCT-ND) | 1 |  | R3
33 | 402 | Digi-key | RHM33KJCT-ND (http://search.digikey.com/scripts/DkSearch/dksus.dll?Detail?name=RHM33KJCT-ND) | 3 |  | R45 R55 R56
500 | 402 | Digi-key | RHM510JCT-ND (http://search.digikey.com/scripts/DkSearch/dksus.dll?Detail?name=RHM510JCT-ND) | 1 |  | R52
50 | 402 | Digi-key | RHM51JCT-ND (http://search.digikey.com/scripts/DkSearch/dksus.dll?Detail?name=RHM51JCT-ND) | 4 |  | R12 R15 R16 R17
82k | 402 | Digi-key | RHM82KJCT-ND (http://search.digikey.com/scripts/DkSearch/dksus.dll?Detail?name=RHM82KJCT-ND) | 2 |  | R49 R50
uclamp0501H | SOD-523 | Digi-key | UCLAMP0501HCT-ND (http://search.digikey.com/scripts/DkSearch/dksus.dll?Detail?name=UCLAMP0501HCT-ND) | 7 |  | D7 D8 D9 D4 D3 D2 D1
UCLAMP33 | SOD-323 | Digi-key | UCLAMP3301DCT-ND (http://search.digikey.com/scripts/DkSearch/dksus.dll?Detail?name=UCLAMP3301DCT-ND) | 2 |  | D10 D11
JUMP | 2x100mil | Digi-key | WM4000-ND (http://search.digikey.com/scripts/DkSearch/dksus.dll?Detail?name=WM4000-ND) | 7 |  | U49 U43 U2 U30 U110 U111 U112
8X100 | 8x100mil | Digi-key | WM4006-ND (http://search.digikey.com/scripts/DkSearch/dksus.dll?Detail?name=WM4006-ND) | 1 |  | U44
NRF24L01-BREAK | 8x100mil | Digi-key | WM4006-ND (http://search.digikey.com/scripts/DkSearch/dksus.dll?Detail?name=WM4006-ND) | 1 |  | U6
10X100 | 11x100mil | Digi-key | WM8080-ND (http://search.digikey.com/scripts/DkSearch/dksus.dll?Detail?name=WM8080-ND) | 2 |  | U17 U20
ZR4040-2.5 | SOT-23 | Digi-key | ZR40402F25CT-ND (http://search.digikey.com/scripts/DkSearch/dksus.dll?Detail?name=ZR40402F25CT-ND) | 1 |  | U42
SFE-MAGJACK | SFE-MAGJACK | sfe |  | 1 |  | U9
SPI_LCD | HIROSE-10 | sfe |  | 1 |  | U34
NXT_CONN | NXT_CONN | mindsensors |  | 1 |  | U25

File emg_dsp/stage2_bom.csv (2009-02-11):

value | footprint | count | references
0.1uf | 0603 | 1 | C71
REG101 | SOIC-8 | 1 | U39
LED | 0603 | 4 | D4 D5 D6 D7
8X2X100 | 2x8x100mil | 2 | U32 U23
1pF | 0402 | 1 | C47
2.2uh | 0805 | 2 | L1 L2
JUMP | 2x100mil | 8 | U25 U40 U33 U2 U10 U11 U1 U13
3.3k | 0603 | 1 | R38
ABM10XTAL | ABM10 | 1 | U14
OMNETICS_36 | omnetics_36 | 1 | U145
47k | 0402 | 4 | R51 R52 R67 R68
0.1uf | 0402 | 15 | C59 C60 C85 C86 C83 C6 C39 C41 C2 C45 C7 C10 C3 C4 C144
2.2uf | 0402 | 11 | C64 C63 C54 C61 C62 C55 C53 C49 C50 C51 C52
2.2k | 0402 | 8 | R26 R27 R28 R29 R30 R31 R32 R33
9.2k | 0402 | 4 | R53 R54 R69 R70
ADM3202 | TSSOP-16 | 1 | U4
BAT54A | SOT-23 | 1 | U9
LMV1032 | microSMD-4 | 96 | U47 U48 U49 U50 U51 U52 U53 U54 U55 U56 U57 U58 U59 U60 U61 U62 U63 U64 U65 U66 U67 U68 U69 U70 U71 U72 U73 U74 U75 U76 U77 U78 U79 U80 U81 U82 U83 U84 U85 U86 U87 U88 U89 U90 U91 U92 U93 U94 U95 U96 U97 U98 U99 U100 U101 U102 U103 U104 U105 U106 U107 U108 U109 U110 U111 U112 U113 U114 U115 U116 U117 U118 U119 U120 U121 U122 U123 U124 U125 U126 U127 U128 U129 U130 U131 U132 U133 U134 U135 U136 U137 U138 U139 U140 U141 U142
150uf | 2x100mil | 1 | C145
UCLAMP33 | SOD-323 | 2 | D8 D9
0.001uf | 0402 | 9 | C40 C11 C14 C8 C26 C27 C25 C142 C141
1uf | 0402 | 22 | C119 C121 C120 C122 C123 C128 C129 C130 C132 C131 C133 C134 C139 C140 C46 C19 C21 C32 C33 C35 C15 C12
10nf | 0603 | 1 | C72
TPS71727 | SC-70-5 | 2 | U26 U27
VAL** | 2.9mm_hole | 5 | 2.9mm_hole 2.9mm_hole 2.9mm_hole 2.9mm_hole 2.9mm_hole
20k | 0402 | 4 | R47 R48 R63 R64
1uf | 0603 | 7 | C73 C70 C69 C68 C67 C77 C79
22K | 0402 | 1 | R19
7pf | 0402 | 1 | C28
22k | 0402 | 4 | R57 R58 R73 R74
68nf | 0402 | 4 | C124 C125 C135 C136
ADSP_JTAG_CON | 7x2x100 | 1 | U12
50k | 0402 | 2 | R15 R10
270k | 0402 | 1 | R8
10uf | 0603 | 6 | C22 C23 C9 C24 C34 C1
MCP3304 | SOIC-16 | 1 | U42
0.012uf | 0402 | 5 | C65 C66 C57 C58 C56
4.7pF | 0402 | 1 | C43
OPA4348 | TSSOP-14 | 2 | U143 U144
FCI_USB_B | FCI_USB_B | 1 | U147
4.7uf | 0603 | 9 | C75 C76 C80 C81 C74 C82 C84 C78 C143
327k | 0402 | 4 | R34 R35 R41 R42
220k | 0402 | 1 | R5
5pf | 0402 | 1 | C30
NRF24L01 | QFN-20 | 1 | U17
TPS62410 | QFN-10 | 1 | U6
ADUM2400 | SOICW-16 | 2 | U46 U45
12.5k | 0402 | 4 | R45 R46 R61 R62
MAX6711 | SC-70-4 | 1 | U20
ferrite | 0402 | 1 | L6
6.5k | 0402 | 4 | R55 R56 R71 R72
8pf | 0402 | 2 | C13 C17
33k | 0402 | 4 | R49 R50 R65 R66
ZR4040-2.5 | SOT-23 | 1 | U44
TLE2426 | SOIC-8 | 1 | U38
uclamp0501 | SOD-523 | 3 | D3 D2 D1
MAX3421E | TQFP-32 | 1 | U3
BF532-160 | MBGA-160 | 1 | U15
RS232_CON | DB9 | 1 | U8
1.5pF | 0402 | 1 | C44
TP | TP | 12 | TP1 TP2 TP4 TP3 TP5 TP6 TP7 TP8 TP10 TP9 TP11 TP12
2.7nH | 0402 | 1 | L5
25 | 0402 | 3 | R16 R14 R13
0.047uf | 0402 | 32 | C87 C88 C89 C90 C91 C92 C93 C94 C95 C96 C97 C98 C99 C100 C101 C102 C103 C104 C105 C106 C107 C108 C109 C110 C111 C112 C113 C114 C115 C116 C117 C118
90k | 0402 | 1 | R7
825k | 0402 | 1 | R6
33 | 0402 | 7 | R3 R4 R1 R22 R23 R24 R25
BAV199 | SOT-363 | 4 | U34 U35 U36 U37
3.9nH | 0402 | 1 | L4
ADCS7476 | SOT-23-6 | 2 | U31 U30
3k | 0402 | 4 | R43 R44 R59 R60
8.2nH | 0402 | 1 | L3
INDUCTOR | 0603 | 2 | L7 L8
0.01uf | 0402 | 12 | C126 C127 C137 C138 C42 C16 C18 C29 C31 C36 C38 C5
10k | 0402 | 7 | R17 R18 R20 R21 R9 R11 R12
33nF | 0402 | 1 | C37
NX3225SA | NDK_XTAL | 1 | U5
2.2nF | 0402 | 1 | C48
100k | 0402 | 1 | R2
TESTCON | 7x100mil | 2 | U21 U16
AT45DB081D | SOIC-8 | 1 | U18
33pf | 0402 | 1 | C20
8X100 | 8x100mil | 1 | U43
ISL28470 | QSOP-28 | 1 | U41
74LCX541 | TSSOP-20 | 2 | U19 U22
ANTENNA | chip_ant | 1 | U146
ADG726 | LFCSP-48 | 1 | U24
THS4281 | SOT-23-5 | 2 | U29 U28
3.3k | 0402 | 4 | R36 R37 R39 R40

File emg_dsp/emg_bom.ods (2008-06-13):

part | price | qty/brd, 16ch | qty/brd, 8ch | per board, 16ch | per brd, 8ch | supplier
high-quality, small AFE
LT1789-1 | 4.3 | 16 | 8 | 68.8 | 34.4 | arrow
BC847BPN | 0.22 | 32 | 16 | 7.04 | 3.52 | digikey
mnr1820 | 0.08 | 2 | 1 | 0.16 | 0.08 | digikey
478-2874-1-ND | 0.57 | 2 | 1 | 1.14 | 0.57 | digikey
LTC6079 | 5.8 | 8 | 4 | 46.4 | 23.2 | digikey
AD7942 | 9.5 | 16 | 8 | 152 | 76 | digikey
 |  |  |  | 275.54 | 137.77
low-cost AFE:
INA2322EA/250 TSSOP-14(PW) | 3.71 | 8 | 4 | 29.68 | 14.84 | mouser
MCP3304 | 4.55 | 4 | 2 | 18.2 | 9.1 | digikey | mouser, newark, arrow also don't have the TSSOP-14
OPA4348AIPWT TSSOP-14 | 1.4 | 8 | 4 | 11.2 | 5.6 | digikey
BC847BPN | 0.22 | 32 | 16 | 7.04 | 3.52 | digikey
mnr18202 | 0.08 | 2 | 1 | 0.16 | 0.08 | digikey
478-2874-1-ND (cap array) | 0.57 | 2 | 1 | 1.14 | 0.57 | digikey
TLE2426CD | 1.3 | 1 | 1 | 1.3 | 1.3 | digikey
 |  |  |  | 68.72 | 35.01
Core & DSP:
ZR40402F25CT-ND (http://search.digikey.com/scripts/DkSearch/dksus.dll?Detail?name=ZR40402F25CT-ND) | 0.63 | 1 | 0.63
REG101 | 2.25 | 1 | 2.25 |  |  | digikey
TPS71733 | 1.35 | 1 | 1.35 |  |  | digikey
ZR40401F25CT SOT-23 | 1.28 | 1 | 1.28 |  |  | digikey
ADUM2400 | 6.16 | 2 | 12.32 |  |  | digikey
MAX253CSA+-ND SOIC-8 (http://search.digikey.com/scripts/DkSearch/dksus.dll?Detail?name=MAX253CSA%2B-ND) | 2.81 | 1 | 2.81 |  |  | digikey
78250MVC | 3.43 | 1 | 3.43 |  |  | mouser
BAT54SFSCT-ND | 0.13 | 4 | 0.52
ADSP-BF536BBCZ-4A-ND 400, lopow (http://search.digikey.com/scripts/DkSearch/dksus.dll?Detail?name=ADSP-BF536BBCZ-4A-ND) | 17.58 | 1 | 17.58 |  |  | digikey
BF536, cheapest, 300Mhz | 11.97 | 0 | 0 |  |  | digikey
BF537, 500Mhz | 23.01 | 0 | 0 |  |  | digikey
BF537, 600Mhz | 28.82 | 0 | 0 |  |  | digikey
BF534, no eth | 16.64 | 0 | 0 |  |  | digikey
SDRAM, 32M, 54VFBGA | 8.75 | 1 | 8.75 |  |  | digikey
SDRAM, 8M, 54TSOP | 2.9 | 0 | 0 |  |  | digikey
AT45DB081D, 8-SOIC | 1.83 | 1 | 1.83 |  |  | digikey
PCD1481CT-ND 3.3uh (http://rocky.digikey.com/scripts/ProductInfo.dll?Site=US&V=10&M=ELJ-PA3R3MF) | 0.27 | 2 | 0.54 |  |  | digikey
FAN2001MPX | 1.38 | 2 | 2.76 |  |  | digikey
NX5032GA 25Mhz | 0.57 | 1 | 0.57 |  |  | digikey
490-3890-1-ND 1uf 0402 (http://search.digikey.com/scripts/DkSearch/dksus.dll?Detail?name=490-3890-1-ND) | 0.07 | 20 | 1.4 |  |  | digikey
495-3265-1-ND 0.1uf X7R 16v | 0.01 | 10 | 0.13 |  |  | digikey
399-1278-1-ND 0.01uf X7R | 0.02 | 10 | 0.2 |  |  | digikey
495-3263-1-ND 10uf 0805 10v (http://search.digikey.com/scripts/DkSearch/dksus.dll?Detail?name=495-3263-1-ND) | 0.13 | 1 | 0.13
PCC2395CT-ND 10uf 0603 (http://search.digikey.com/scripts/DkSearch/dksus.dll?Detail?name=PCC2395CT-ND) | 0.36 | 5 | 1.81 |  |  | digikey
493-1021-ND 100uf 10v | 0.11 | 4 | 0.44 |  |  | digikey
74LCX541MTCXCT-ND (http://search.digikey.com/scripts/DkSearch/dksus.dll?Detail?name=74LCX541MTCXCT-ND) | 0.52 | 2 | 1.04 |  |  | digikey
ADM6713SAKS | 0.78 | 1 | 0.78 |  |  | digikey
 |  |  | 0 |  |  | digikey
74LV594A TSSOP-16 (PW) | 1.04 | 1 | 1.04 |  |  | mouser
 |  |  |  | 63.59
Interface |  |  | 0
Ethernet -- |  |  | 0
pulsejack JK0-0025Nl | 7.83 | 0 | 0 |  |  | digikey
chinese magjack | 1.95 | 1 | 1.95 |  |  | sfe
LAN83C185 | 5.13 | 1 | 5.13
NDS336P | 0.5 | 1 | 0.5
UCLAMP0501HCT-ND 3.3v zener | 0.45 | 4 | 1.8
 |  |  | 0 | 9.38
USB -- |  |  | 0
MAX3421EEHJ TQFP-32 | 11.1 | 1 | 11.1 |  |  | digikey
609-1039-ND connector | 1.04 | 1 | 1.04 |  |  | digikey
644-1047-1-ND Crystal, 12mhz (http://rocky.digikey.com/scripts/ProductInfo.dll?Site=US&V=644&M=NX3225SA-12.000000MHZ) | 0.75 | 1 | 0.75 |  |  | digikey
PCD2116CT-ND 57UH (http://search.digikey.com/scripts/DkSearch/dksus.dll?Detail?name=PCD2116CT-ND) | 0.86 | 1 | 0.86 |  |  | digikey
S-8354A50MC stepup w/shdn SOT-23-5 728-1036-1-ND | 0.9 | 1 | 0.9 |  |  | digikey
CAT32TDI-TE7 | 0.13 | 2 | 0.26 |  |  | digikey
UCLAMP0501HCT-ND | 0.58 | 3 | 1.74
F2110CT-ND 200/500ma 1206 | 0.4 | 1 | 0.4
 |  |  |  | 17.05
LCD --
LCD (SPI, 128x128,1.2”) | 19.95 | 1 | 19.95 |  |  | sfe
LCD connector | 1.95 | 1 | 1.95 |  |  | sfe
CAT32TDI-TE7 | 0.8 | 1 | 0.8 |  |  | mouser
PCD1238CT-ND 6.8uh 1008 | 0.27 | 1 | 0.27 |  |  | digikey
BAT54A | 0.13 | 1 | 0.13 |  |  | digikey
 |  |  | 0 | 23.1
RS-232 |  |  | 0
ADM3202ARUZ lvl cnv 16-TSSOP | 1.35 | 1 | 1.35 |  |  | digikey
A35114 DB9 conn | 1.34 | 1 | 1.34 |  |  | digikey
NDS336P | 0.5 | 1 | 0.5
 |  |  | 0 | 3.19
NXT |  |  | 0
NXT connector | 0.99 | 1 | 0.99 |  |  | mindsensors.com
 |  |  | 0
audio |  |  | 0
TDA7535013 | 5.4 | 1 | 5.4 |  |  | digikey
OPA4348 | 1.49 | 1 | 1.49 |  |  | digikey
CP1-3545-ND (http://rocky.digikey.com/scripts/ProductInfo.dll?Site=US&V=102&M=SJ1-3545) | 0.65 | 1 | 0.65 |  |  | digikey

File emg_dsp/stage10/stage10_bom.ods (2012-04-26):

value | footprint | count | Digi-key | references
0.1uf | 402 | 51 | 490-1318-1-ND (http://search.digikey.com/us/en/products/GRM155R61A104KA01D/490-1318-1-ND/587923) | C64 C63 C76 C81 C2 C38 C12 C9 C14 C15 C50 C56 C55 C37 C33 C8 C6 C10 C11 C42 C36 C31 C28 C26 C49 C47 C13 C46
200 | 402 | 41 | P200JCT-ND (http://search.digikey.com/us/en/products/ERJ-2GEJ201X/P200JCT-ND/146925) | R41 R40 R42 R35 R36 R53 R52 R54 R47 R48 R65 R64 R66 R59 R60 R77 R76 R78 R71 R72 R79 R80
2.2uf | 402 | 22 | 445-6847-1-ND (http://search.digikey.com/us/en/products/C1005X5R0J225K/445-6847-1-ND/2619209) | C37 C36 C35 C38 C42 C45 C44 C43 C46 C50 C53 C52 C51 C54 C58 C61 C60 C59 C62 C66
1uf | 402 | 21 | 490-3890-1-ND (http://search.digikey.com/us/en/products/GRM155R61A105KE15D/490-3890-1-ND/965932) | C69 C66 C72 C85 C91 C40 C18 C7 C48 C32 C5 C3 C60 C39 C41 C61 C62 C73
130 | 402 | 20 | P130JCT-ND (http://search.digikey.com/us/en/products/ERJ-2GEJ131X/P130JCT-ND/146865) | R36 R37 R42 R43 R44 R45 R46 R47 R48 R49 R104 R107 R105 R108 R106 R109 R103 R114 R132 R133
50k | 402 | 15 | P49.9KLCT-ND (http://search.digikey.com/us/en/products/ERJ-2RKF4992X/P49.9KLCT-ND/194427) | R8 R21 R22 R23 R18 R24 R19 R20 R25 R29 R30 R50 R51 R53 R55
22k | 402 | 14 | P22KJCT-ND (http://search.digikey.com/us/en/products/ERJ-2GEJ223X/P22KJCT-ND/146939) | R30 R21 R17 R26 R29 R23 R81 R82
10k | 402 | 10 | P10KJCT-ND (http://search.digikey.com/us/en/products/ERJ-2GEJ103X/P10KJCT-ND/146734) | R41 R26 R27 R28 R15 R17 R128 R115 R134 R135
33 | 402 | 9 | P33JCT-ND (http://search.digikey.com/us/en/products/ERJ-2GEJ330X/P33JCT-ND/146979) | R16 R2 R1 R7 R52 R13 R14 R54 R56
0.01uf | 402 | 6 | 490-1312-1-ND (http://search.digikey.com/us/en/products/GRM155R71E103KA01D/490-1312-1-ND/587934) | C35 C30 C27 C25
49.9 | 402 | 5 | P49.9LCT-ND (http://search.digikey.com/us/en/products/ERJ-2RKF49R9X/P49.9LCT-ND/194426) | R35 R34 R33 R32 R121
24.9k | 402 | 5 | P24.9KLCT-ND (http://search.digikey.com/us/en/products/ERJ-2RKF2492X/P24.9KLCT-ND/194285) | R120 R38 R50 R62 R74
15k | 402 | 4 | P15KJCT-ND (http://search.digikey.com/us/en/products/ERJ-2GEJ153X/P15KJCT-ND/146879) | R37 R49 R61 R73
5k | 402 | 4 | P4.99KLCT-ND (http://search.digikey.com/us/en/products/ERJ-2RKF4991X/P4.99KLCT-ND/194389) | R74 R73 R76 R75
7k | 402 | 5 | P6.98KLCT-ND (http://search.digikey.com/us/en/products/ERJ-2RKF6981X/P6.98KLCT-ND/194470) | R39 R51 R63 R75 R129
7pf | 402 | 4 | 490-3107-1-ND (http://search.digikey.com/us/en/products/GJM1555C1H7R0CB01D/490-3107-1-ND/702373) | C16 C23 C22 C21
0.001uf | 402 | 5 | 490-1303-1-ND | C26 C24 C23 C68 C67 ** incorrect p/n originally.
100pf | 402 | 3 | 445-6845-1-ND (http://search.digikey.com/us/en/products/C1005C0G1E101J/445-6845-1-ND/2619207) | C75 C87 C51
15pf | 402 | 3 | 490-1280-1-ND (http://search.digikey.com/us/en/products/GRM1555C1H150JZ01D/490-1280-1-ND/587885) | C54 C53 C52
ferrite | 402 | 3 | 490-1006-1-ND (http://search.digikey.com/us/en/products/BLM15AG601SN1D/490-1006-1-ND/584454) | L3 L4 L6
402 | 402 | 2 | P402LCT-ND (http://search.digikey.com/us/en/products/ERJ-2RKF4020X/P402LCT-ND/194392) | R126 R122
33pf | 402 | 2 | 490-3220-1-ND (http://search.digikey.com/us/en/products/GRM1555C1H330JZ01D/490-3220-1-ND/702761) | C17 C11
4.7pF | 402 | 2 | 490-3100-1-ND (http://search.digikey.com/us/en/products/GJM1555C1H4R7CB01D/490-3100-1-ND/702366) | C17 C28
47pf | 402 | 2 | 490-1287-1-ND (http://search.digikey.com/us/en/products/GRM1555C1H470JZ01D/490-1287-1-ND/587893) | C74 C77
80k | 402 | 2 | P80.6KLCT-ND (http://search.digikey.com/us/en/products/ERJ-2RKF8062X/P80.6KLCT-ND/194532) | R117 R118
90k | 402 | 2 | P90.9KLCT-ND (http://search.digikey.com/us/en/products/ERJ-2RKF9092X/P90.9KLCT-ND/194556) | R5 R6
1.27k | 402 | 1 | P1.27KLCT-ND (http://search.digikey.com/us/en/products/ERJ-2RKF1271X/P1.27KLCT-ND/194098) | R119
1.5pF | 402 | 1 | 478-5992-1-ND (http://search.digikey.com/us/en/products/04025U1R5BAT2A/478-5992-1-ND/2208917) | C29
12.1k | 402 | 1 | P12.1KLCT-ND (http://search.digikey.com/us/en/products/ERJ-2RKF1212X/P12.1KLCT-ND/79807) | R31
13.3k | 402 | 1 | P13.3KLCT-ND (http://search.digikey.com/us/en/products/ERJ-2RKF1332X/P13.3KLCT-ND/194165) | R131
165k | 402 | 1 | P165KLCT-ND (http://search.digikey.com/us/en/products/ERJ-2RKF1653X/P165KLCT-ND/194205) | R15
180k | 402 | 1 | P180KJCT-ND (http://search.digikey.com/us/en/products/ERJ-2GEJ184X/P180KJCT-ND/146891) | R3
1pF | 402 | 1 | 490-3083-1-ND (http://search.digikey.com/us/en/products/GJM1555C1H1R0CB01D/490-3083-1-ND/702349) | C31
2.2nF | 402 | 1 | 490-1305-1-ND (http://search.digikey.com/us/en/products/GRM155R71H222KA01D/490-1305-1-ND/587945) | C32
2.7nH | 402 | 1 | PCD1851CT-ND (http://search.digikey.com/us/en/products/ELJ-QF2N7DF/PCD1851CT-ND/674200) | L5
200k | 402 | 1 | P200KJCT-ND (http://search.digikey.com/us/en/products/ERJ-2GEJ204X/P200KJCT-ND/146927) | R13
270k | 402 | 1 | P270KJCT-ND (http://search.digikey.com/us/en/products/ERJ-2GEJ274X/P270KJCT-ND/146951) | R16
2k | 402 | 1 | P2.0KJCT-ND (http://search.digikey.com/us/en/products/ERJ-2GEJ202X/P2.0KJCT-ND/146957) | R124
3.9nH | 402 | 1 | 732-1711-1-ND (http://search.digikey.com/us/en/products/744765039A/732-1711-1-ND/1994291) | L4
41.2k | 402 | 1 | P41.2KLCT-ND (http://search.digikey.com/us/en/products/ERJ-2RKF4122X/P41.2KLCT-ND/194395) | R130
47nf | 402 | 2 | 490-3270-1-ND (http://search.digikey.com/us/en/products/GRM155F51E473ZA01D/490-3270-1-ND/702811) | C82 C25
59k | 402 | 1 | P59.0KLCT-ND (http://search.digikey.com/us/en/products/ERJ-2RKF5902X/P59.0KLCT-ND/194461) | R116
6.8nf | 402 | 1 | 445-4922-1-ND (http://search.digikey.com/us/en/products/C1005X7R1H682K/445-4922-1-ND/2093536) | C88
725k | 402 | 1 | P732KLCT-ND (http://search.digikey.com/us/en/products/ERJ-2RKF7323X/P732KLCT-ND/194512) | R14
7pf | 402 | 1 | 490-3107-1-ND (http://search.digikey.com/us/en/products/GJM1555C1H7R0CB01D/490-3107-1-ND/702373) | C14
8.2nH | 402 | 1 | 732-1719-1-ND (http://search.digikey.com/us/en/products/744765082A/732-1719-1-ND/1994299) | L3
810k | 402 | 1 | P806KLCT-ND (http://search.digikey.com/us/en/products/ERJ-2RKF8063X/P806KLCT-ND/194534) | R4
10uf | 603 | 14 | 587-2562-1-ND (http://search.digikey.com/us/en/products/LMK107BJ106MALTD/587-2562-1-ND/2269355) | C65 C19 C20 C4 C43 C29 C45 C44
49.9 | 603 | 1 | 541-49.9SCT-ND (http://search.digikey.com/us/en/products/CRCW060349R9FKEAHP/541-49.9SCT-ND/2222759) | R127
50k | 603 | 1 | PNM0603-50KBCT-ND | R123
475-2558 | D0603 | 17 | 475-2558-1-ND (http://search.digikey.com/us/en/products/LY%20Q976-P1S2-36/475-2558-1-ND/1802685) | D36 D34 D32 D30 D28 D26 D24 D22 D35 D33 D31 D29 D27 D25 D23 D1
MAX6711Z | SC-70-4 | 2 | MAX6711ZEXS+TCT-ND (http://search.digikey.com/us/en/products/MAX6711ZEXS%2BT/MAX6711ZEXS%2BTCT-ND/1173297)
MIC5365-2.7 | SC-70-5 | 4 | 576-3319-1-ND (http://search.digikey.com/us/en/products/MIC5365-2.7YC5%20TR/576-3319-1-ND/1974137) | U15 U22 U29 U36
TC1016-3.0 | SC-70-5 | 4 | TC1016-3.0VLTCT-ND (http://search.digikey.com/us/en/products/TC1016-3.0VLTTR/TC1016-3.0VLTCT-ND/669507) | U16 U23 U30 U37
MIC5365-2.5 | SC-70-5 | 2 | 576-3185-1-ND (http://search.digikey.com/us/en/products/MIC5365-2.5YC5%20TR/576-3185-1-ND/1868222) | U14 U27
BAS16 | SOT-23 | 2 | 568-7979-1-ND (http://search.digikey.com/us/en/products/BAS16,235/568-7979-1-ND/2762669) | D19 D20
TLV431ACD | SOT-23 | 1 | 296-18912-1-ND (http://search.digikey.com/us/en/products/TLV431ACDBZR/296-18912-1-ND/863991) | U41
ADCS7476 | SOT-23-6 | 4 | ADCS7476AIMFCT-ND (http://search.digikey.com/us/en/products/ADCS7476AIMF%2FNOPB/ADCS7476AIMFCT-ND/568525) | U19 U26 U33 U40
FDC2512 | SOT-23-6 | 1 | FDC2512CT-ND (http://search.digikey.com/us/en/products/FDC2512/FDC2512CT-ND/2094414) | U38
USBLC6 | SOT-23-6 | 1 | 497-5235-6-ND | U11
** Hand-place SMD **
0.01uf | 805 | 1 | 478-6356-1-ND (http://search.digikey.com/us/en/products/08052C103KAZ2A/478-6356-1-ND/2512192) | C83
47uf | 1206 | 2 | 445-6003-1-ND (http://search.digikey.com/us/en/products/C3216X5R1C476M/445-6003-1-ND/2444044) | C90 C89
0.56 | 1206 | 1 | RL16R.56FCT-ND (http://search.digikey.com/us/en/products/RL1632R-R560-F/RL16R.56FCT-ND/714532) | R125
4.7uf | 1210 | 5 | 445-6042-1-ND (http://search.digikey.com/us/en/products/C3225X7S2A475K/445-6042-1-ND/2444083) | C80 C86 C84 C78 C93
2.2uh | 1210 | 4 | 587-2165-6-ND (http://search.digikey.com/us/en/products/BRL3225T2R2M/587-2165-6-ND/2002956) | L1 L2
4.7uh | 1210 | 1 | 587-1624-1-ND (http://search.digikey.com/us/en/products/CBC3225T4R7MR/587-1624-1-ND/1008239) | L5
150uf | 2917 | 3 | 495-2225-1-ND (http://search.digikey.com/us/en/products/B45196H2157M409/495-2225-1-ND/770391) | C70 C71 C1
ABM10XTAL-16 | ABM10 | 1 | 535-10923-1-ND (http://search.digikey.com/us/en/products/ABM10-16.000MHZ-D30-T3/535-10923-1-ND/2624174) | U5
ABM10XTAL-24 | ABM10 | 1 | 535-9622-1-ND (http://search.digikey.com/us/en/products/ABM10-24.000MHZ-8-7-A15-T/535-9622-1-ND/1237089) | U12
ABM10XTAL-25 | ABM10 | 1 | 535-9095-1-ND (http://search.digikey.com/us/en/products/ABM10-25.000MHZ-E20-T/535-9095-1-ND/675612) | U9
ANTENNA | chip_ant | 1 |  | U12
MBRS540T3 | DO-214AC | 1 | SS16FSCT-ND (http://search.digikey.com/us/en/products/SS16/SS16FSCT-ND/2053174) | D21
MURA120 | DO-214AC | 1 | MURA120T3GOSCT-ND (http://search.digikey.com/us/en/products/MURA120T3G/MURA120T3GOSCT-ND/1139949) | D18
SMAJ58A | DO-214AC | 1 | SMAJ58ABCT-ND (http://search.digikey.com/us/en/products/SMAJ58A/SMAJ58ABCT-ND/2253531) | D17
BF532-160 | MBGA-160 | 1 | ADSP-BF532SBBCZ400-ND (http://search.digikey.com/us/en/products/ADSP-BF532SBBCZ400/ADSP-BF532SBBCZ400-ND/936535) | U6
BF527 | MBGA-208 | 1 | ADSP-BF527KBCZ-6A-ND (http://search.digikey.com/us/en/products/ADSP-BF527KBCZ-6A/ADSP-BF527KBCZ-6A-ND/2077092) | U13
AD5663 | MSOP-10 | 1 | AD5663ARMZ-ND (http://search.digikey.com/us/en/products/AD5663ARMZ/AD5663ARMZ-ND/1120031) | U28
OMNETICS_36 | omnetics_36_dual | 4 |  | U14 U21 U28 U35
9X100 | omnetics_9 | 12 |  | U18 U20 U25 U27 U32 U34 U39 U41 U3
TPS62410 | QFN-10 | 2 | 296-25488-1-ND (http://search.digikey.com/us/en/products/TPS62410DRCR/296-25488-1-ND/2193060) | U4
NRF24L01 | QFN-20 | 1 |  | U8
LAN8710A | QFN-32 | 1 | 638-1083-ND | U17
RHA2132 | QFN-56 | 4 |  | U42 U43 U44 U45
LM4808 | SOIC-8 | 1 | LM4808M-ND | U29
SST25VF040B | SOIC-8 | 2 | SST25VF040B-80-4I-SAE-ND (http://search.digikey.com/us/en/products/SST25VF040B-80-4I-SAE/SST25VF040B-80-4I-SAE-ND/2299395) | U15
TPS23753 | TSSOP-14 | 1 | 296-23547-5-ND (http://search.digikey.com/us/en/products/TPS23753PW/296-23547-5-ND/1880904) | U37
ADM3202 | TSSOP-16 | 1 | ADM3202ARUZ-ND (http://search.digikey.com/us/en/products/ADM3202ARUZ/ADM3202ARUZ-ND/820172) | U3
74LCX541 | TSSOP-20 | 4 | 74LCX541MTCXCT-ND (http://search.digikey.com/us/en/products/74LCX541MTCX/74LCX541MTCXCT-ND/965512) | U18 U23 U22 U33
MT48LC16M16A2 | VFBGA-54 | 1 | 557-1220-1-ND (http://search.digikey.com/us/en/products/MT48LC16M16A2BG-7E:D%20TR/557-1220-1-ND/1531201) | U7
** Through-hole **
POE13W | POE13W | 1 | 513-1105-1-ND (http://search.digikey.com/us/en/products/POE13W3X5.0-R/513-1105-1-ND/754612) | U40
POE-JACK | POE-JACK | 1 | A99645-ND | U36
NRF24L01-BREAK | 8x100mil | 5 | 609-3406-ND (http://search.digikey.com/us/en/products/68002-408HLF/609-3406-ND/1487482) | U24 U25 U26 U21 U35
ADSP_JTAG_CON | 7x2x100 | 2 | A26576-ND (http://search.digikey.com/us/en/products/87215-4/A26576-ND/298249) | U16 U34
63uf | 2x200mil | 1 | 493-1665-ND | C92
EN_VCC | 2x100mil | 4 | A26543-ND (http://search.digikey.com/us/en/products/87224-2/A26543-ND/298247) | U8
FOD817A | DIP-4 | 1 | FOD817A-ND (http://search.digikey.com/us/en/products/FOD817A/FOD817A-ND/1049821) | U39
RS232_CON | DB9 | 1 | A32115-ND | U1
GT12 | GT12MABE | 1 | CKN9048-ND
FCI_USB_B | FCI_USB_B | 1 | 609-1039-ND | U6
NHD-0216KZW | NHD-0216KZW | 1 | NHD-0216KZW-AB5-ND (http://search.digikey.com/us/en/products/NHD-0216KZW-AB5/NHD-0216KZW-AB5-ND/2626456)

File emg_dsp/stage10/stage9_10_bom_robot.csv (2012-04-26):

value | footprint | count
0.1uf | 402 | 51
200 | 402 | 41
2.2uf | 402 | 22
1uf | 402 | 21
130 | 402 | 20
50k | 402 | 15
22k | 402 | 14
10k | 402 | 10
33 | 402 | 9
0.01uf | 402 | 6
49.9 | 402 | 5
24.9k | 402 | 5
15k | 402 | 4
5k | 402 | 4
7k | 402 | 5
7pf | 402 | 4
0.001uf | 402 | 5
100pf | 402 | 3
15pf | 402 | 3
ferrite | 402 | 3
402 | 402 | 2
33pf | 402 | 2
4.7pF | 402 | 2
47pf | 402 | 2
80k | 402 | 2
90k | 402 | 2
1.27k | 402 | 1
1.5pF | 402 | 1
12.1k | 402 | 1
13.3k | 402 | 1
165k | 402 | 1
180k | 402 | 1
1pF | 402 | 1
2.2nF | 402 | 1
2.7nH | 402 | 1
200k | 402 | 1
270k | 402 | 1
2k | 402 | 1
3.9nH | 402 | 1
41.2k | 402 | 1
47nf | 402 | 2
59k | 402 | 1
6.8nf | 402 | 1
725k | 402 | 1
7pf | 402 | 1
8.2nH | 402 | 1
810k | 402 | 1
10uf | 603 | 14
49.9 | 603 | 1
50k | 603 | 1
475-2558 | D0603 | 17
MAX6711Z | SC-70-4 | 2
MIC5365-2.7 | SC-70-5 | 4
TC1016-3.0 | SC-70-5 | 4
MIC5365-2.5 | SC-70-5 | 2
BAS16 | SOT-23 | 2
TLV431ACD | SOT-23 | 1
ADCS7476 | SOT-23-6 | 4
FDC2512 | SOT-23-6 | 1
USBLC6 | SOT-23-6 | 1

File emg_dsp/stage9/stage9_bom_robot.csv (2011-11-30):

value | footprint | count | references
0.1uf | 402 | 23 | C41 C40 C39 C49 C48 C47 C57 C56 C55 C65 C64 C63 C3 C8 C16 C18 C19 C20 C21 C22 C4 C2 C68
200 | 402 | 22 | R41 R40 R42 R35 R36 R53 R52 R54 R47 R48 R65 R64 R66 R59 R60 R77 R76 R78 R71 R72 R79 R80
2.2uf | 402 | 20 | C37 C36 C35 C38 C42 C45 C44 C43 C46 C50 C53 C52 C51 C54 C58 C61 C60 C59 C62 C66
22k | 402 | 9 | R30 R28 R21 R17 R26 R29 R23 R81 R82
15k | 402 | 4 | R37 R49 R61 R73
24.9k | 402 | 4 | R38 R50 R62 R74
7k | 402 | 4 | R39 R51 R63 R75
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

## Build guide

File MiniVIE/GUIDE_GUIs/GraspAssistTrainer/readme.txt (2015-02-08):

MATLAB Compiler

1. Prerequisites for Deployment 

. Verify the MATLAB runtime is installed and ensure you    
  have installed version 8.4 (R2014b).   

. If the MATLAB runtime is not installed, do the following:
  (1) enter
  
      >>mcrinstaller
      
      at MATLAB prompt. The MCRINSTALLER command displays the 
      location of the MATLAB runtime installer.

  (2) run the MATLAB runtime installer.

Or download the Windows 64-bit version of the MATLAB runtime for R2014b 
from the MathWorks Web site by navigating to

   http://www.mathworks.com/products/compiler/mcr/index.html

For more information about the MATLAB runtime and the MATLAB runtime installer, see 
Distribution to End Users in the MATLAB Compiler documentation  
in the MathWorks Documentation Center.    

NOTE: You will need administrator rights to run MCRInstaller. 

2. Files to Deploy and Package

Files to package for Standalone 
================================
-GraspAssistTrainer.ctf (component technology file)
-GraspAssistTrainer.exe
-MCRInstaller.exe 
   -if end users are unable to download the MATLAB runtime using the above  
    link, include it when building your component by clicking 
    the "Runtime downloaded from web" link in the Deployment Tool
-This readme file 

3. Definitions

For information on deployment terminology, go to 
http://www.mathworks.com/help. Select MATLAB Compiler >   
Getting Started > About Application Deployment > 
Application Deployment Terms in the MathWorks Documentation 
Center.

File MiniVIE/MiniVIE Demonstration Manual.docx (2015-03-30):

# MiniVIE Demonstration Setup Manual

This manual goes through the process necessary to download the MiniVIE open-source project code package and run the MiniVIE Demonstration completely.

## Section I: Setting up the code Repository

### Importing MATLAB Code

This section details how to extract code from the internet and import it to MATLAB.

Note: While steps 1-21 are specific to the MiniVIE Demonstration, they can be applied to any download of files from the internet imported into MATLAB.

1. Open up a web browser and navigate to the link: https://github.com/tlh24/myopen
2. Click the “Download ZIP” button:

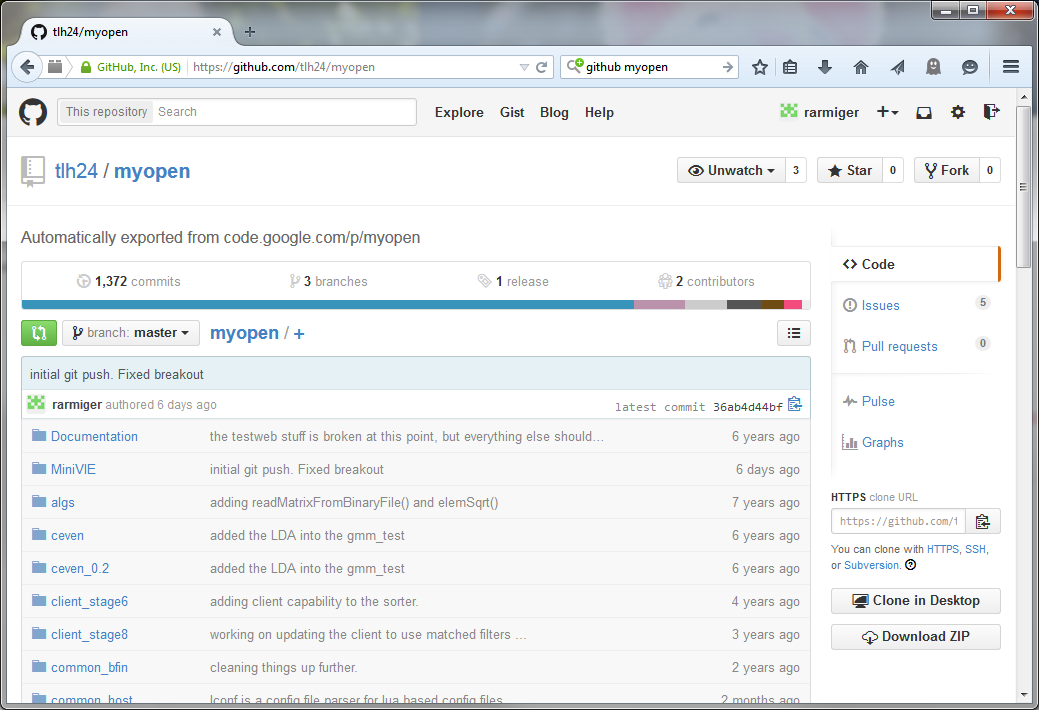
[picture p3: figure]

3. Save the file to a folder on your computer (e.g. the Downloads folder)
4. Open the folder containing the ZIP file
5. Right-click the ZIP file and select Extract All…
6. Select destination “c:\git” and then Extract:

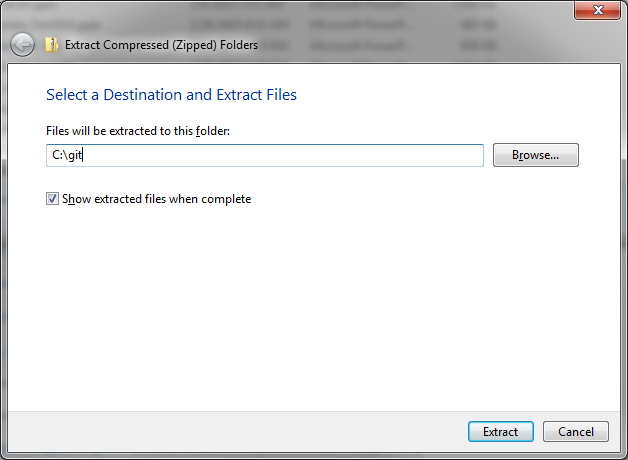
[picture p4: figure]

7. Rename the folder myopen-master to myopen

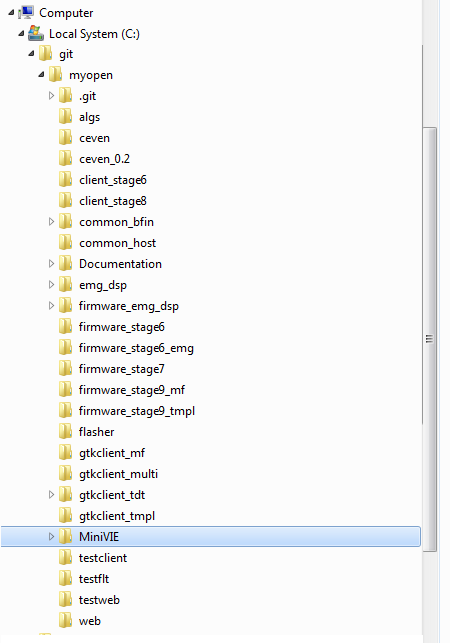
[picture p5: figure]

Default Folder Structure

### Setting up git

1. If you are a developer or want to stay current with the latest changes, you can install a git tool such as: https://windows.github.com/
2. The repository can then be linked to the tool and any changes can be downloaded pulled from the server

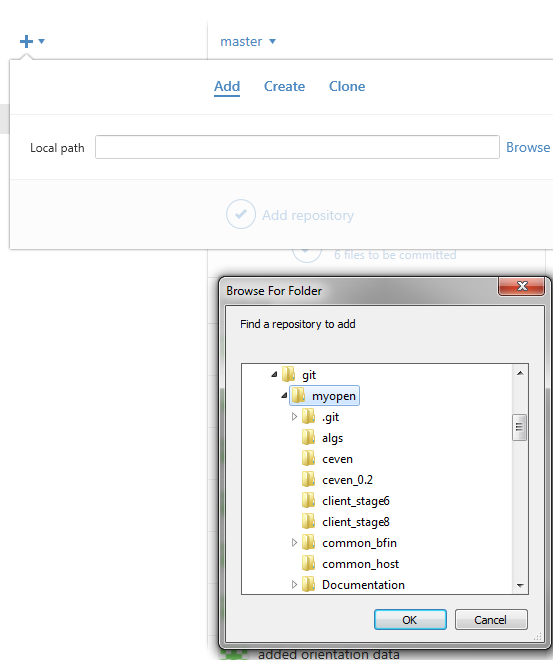
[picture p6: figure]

3. GitHub repository manager. The github manager allows you to obtain updates using the ‘Sync’ button in the top-right corner

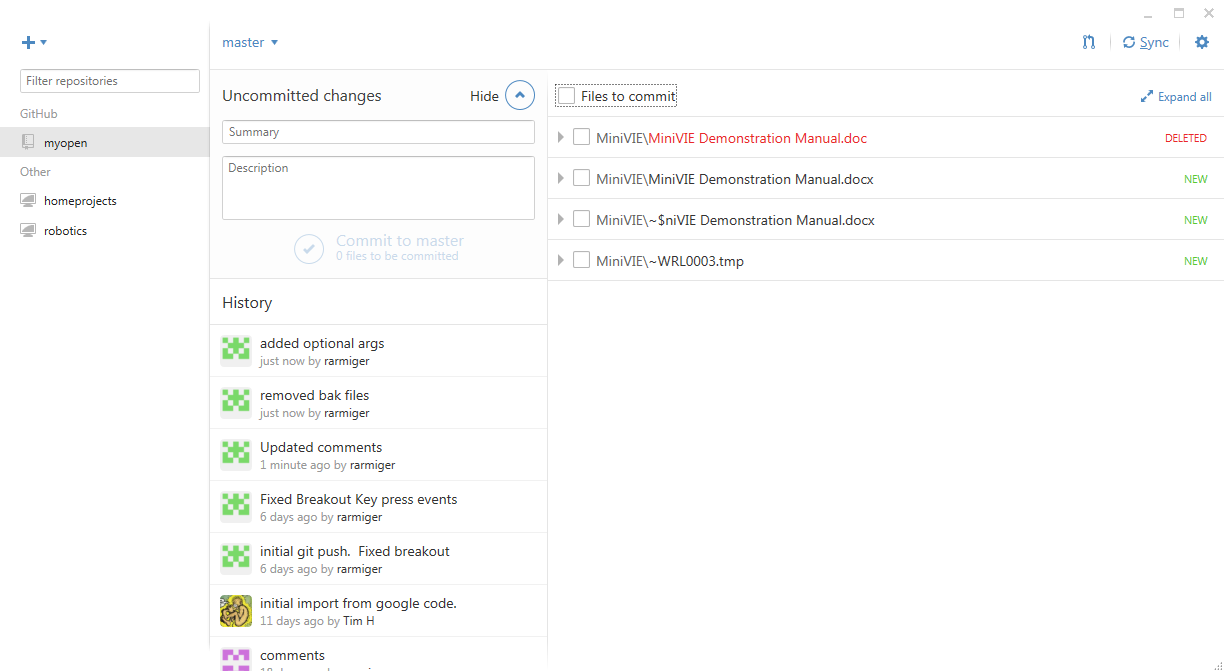
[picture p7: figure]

## Section II: MATLAB First Time Setup

1. Open MATLAB
2. Navigate to the C:\git\myopen\MiniVIE folder
3. Run the command: >> MiniVIE.createShortcuts

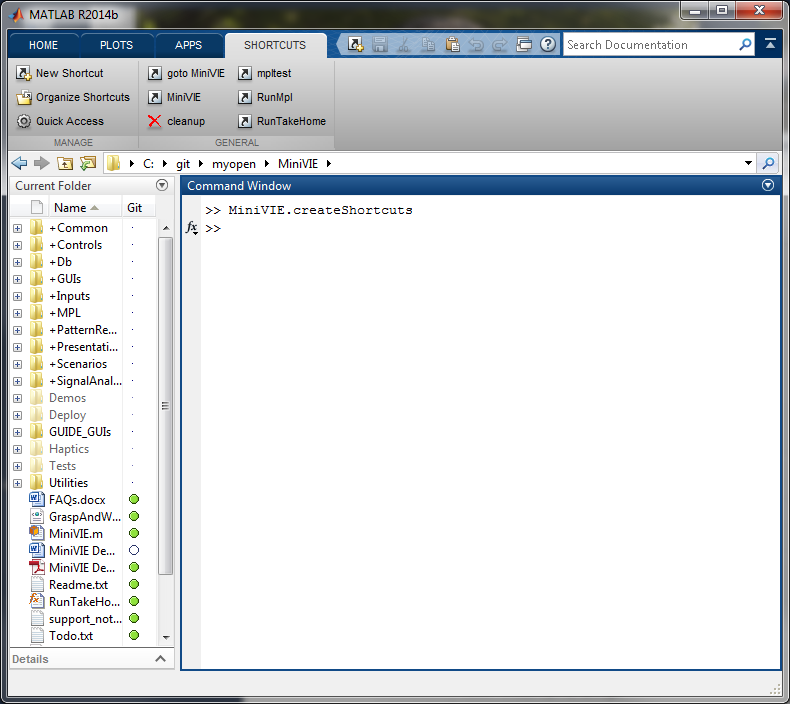
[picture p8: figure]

4. This will generate a group of links for quick access to MiniVIE tools

## Section III: Running the MiniVIE

1. Open MATLAB
2. From the shortcuts menu select ‘MiniVIE’
3. A window titled MiniVIE Configuration Utility will open with the settings for the MiniVIE program:

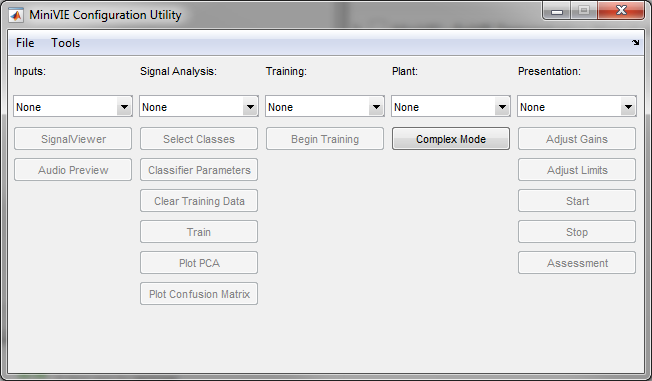
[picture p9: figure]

4. In the Inputs drop-down menu, select Signal Simulator:

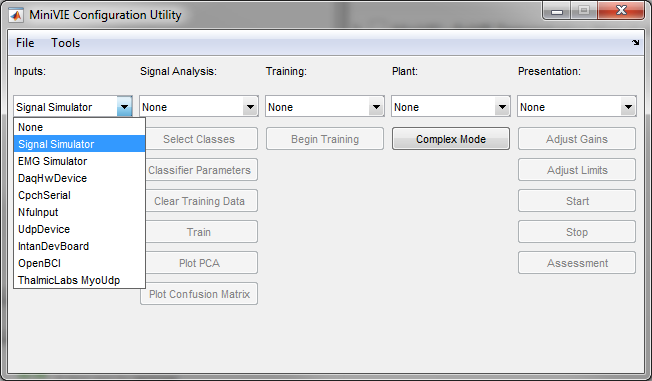
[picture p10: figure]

5. A EMG Simulator dialogue window should open.
6. While the user is in this selected open window, pressing any of the following keys will cause a number to appear as the current pattern: keys a, s, d, f, q, w, e, r, z, x, c, v.

(Key: a) (Key: v)

Note: Ensure that the Simulator Window is the ActiveWindow on your systems so that key presses are directed toward MATLAB

7. Under Signal Analysis, select LDA Classifier:

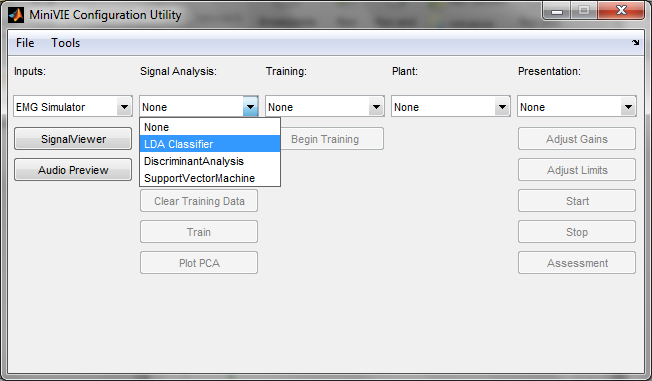
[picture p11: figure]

8. Next click on the Select Classes button and a new window will open:

Note: Each class selected is a movement the arm will perform. Using the EMG Simulator, a maximum of 8 movements can be selected at a time. In addition to the 8 movements, “No Movement” should also always be selected so there is a baseline for each training session.

9. Select the classes that are to be trained. Then close the window:

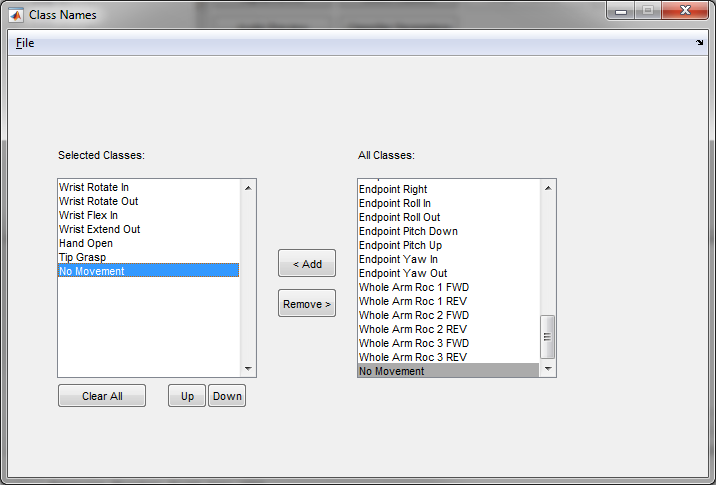
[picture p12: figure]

10. Under Training, select Simple Trainer:

Note: Do not select any options for Plant or Presentation drop-down menus prior to beginning training.

11. Select the desired settings for simple training when the dialogue box opens.

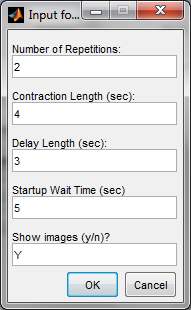
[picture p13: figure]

## Section IV: Training

This section goes through step by step of the training process. Before beginning the actual training process, the user should read the entire following section to understand the required actions of the user during the rapid training process.

Note: Record ahead of time (for future use in the MiniVIE demonstration) which key the user will assign to each movement class.

1. A window will pop up with a 3 second countdown:

Note: as soon as the countdown begins, the user must select the EMG Simulator window (window should be maximized and click on this window to highlight it as the selected window). Keep this as the selected open window for the duration of the training process.

2. The Trainer will then begin training with the first of the 8 selected classes. There will be a period of a few seconds (represented by a red loading bar) allowing for preparation:

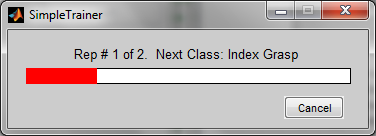
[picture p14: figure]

3. During this time, press and hold down one of the designated 8 keyboard keys (a, s, d, f, q, w, e, r) which will later be assigned to the selected class. The Current Pattern will change pattern number. Continue to hold down the selected key and do not release the keyboard key throughout the next step:
4. The bar will then change from red to green and retreat to the left. During this time, the trainer program is collecting a signal from the selected keyboard key and matching that signal to the command being trained:

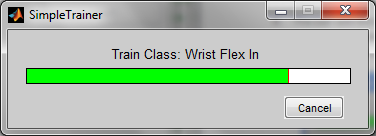
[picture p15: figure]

5. When the data is collected, the training will transition to the next class. During the preparation period, switch the keyboard key selected (ie., release the first key chosen, and choose another of the remaining 7 key options). This should be represented by a change in the Current Pattern number:
6. Hold down the chosen keyboard key until the training for the current class is complete:

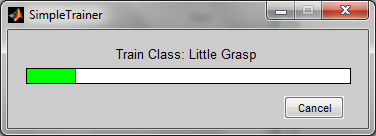
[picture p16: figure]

7. Repeat steps 4 - 6 for the remaining classes, except for the “No Movement” class.
8. For the training of the “No Movement” class, do not press any keyboard key:

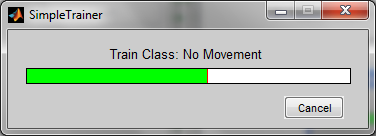
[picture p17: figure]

Note: The reason for not depressing a key during the “No Movement” class is that during the demonstration, the object (the arm for the MiniVIE demonstration) will remain still while it is not receiving signals. Otherwise, the user would have to hold down a key to keep the object still.

9. Training is now completed:
10. When prompted with the window below, save the data gathered in this training session:

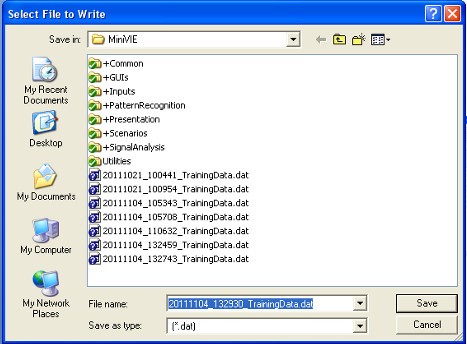
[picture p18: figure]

11. Open the MATLAB window. In the MATLAB Command Window, the accuracy of the results from the training session is shown. Check the results and if they are not 100% for each command, return to step 1 and perform a new training session:

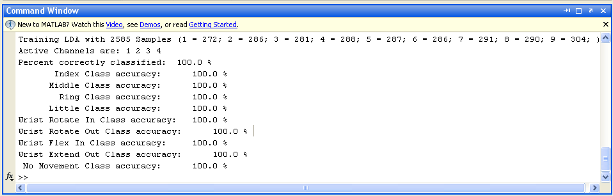
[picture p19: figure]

12. Once the user has read the training instructions above, select Begin Training in the MiniVIE Configuration Utility window:

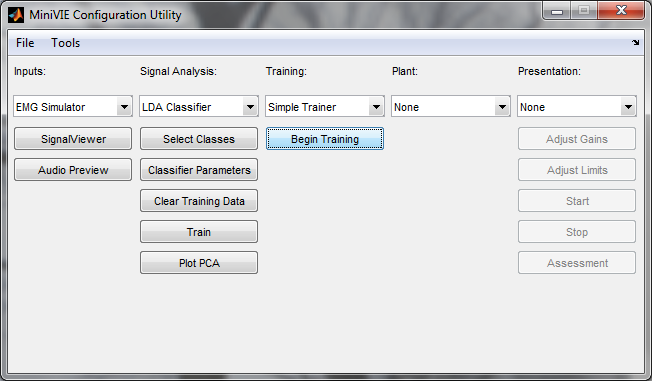
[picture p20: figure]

## Section V: Running the MiniVIE Demonstration

This section explains how to run the MiniVIE Demonstration once training is complete.

1. Return to the MiniVIE Configuration Utility window, and in the Presentation drop-down menu, select MiniV. A window with an animated human arm will open:
2. Select the EMG Simulator window.
3. Press one of the 8 keyboard keys associated with the eight movement classes:

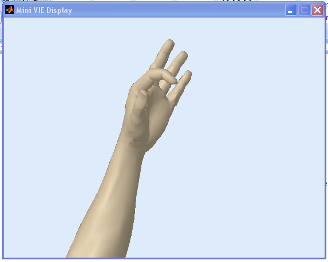
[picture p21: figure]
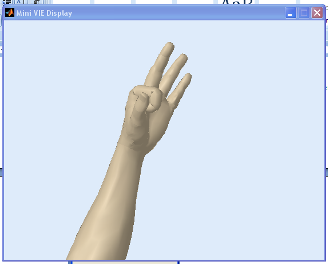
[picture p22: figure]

4. Repeat step #3 with each of the remaining movement classes, to verify that the animated arm responds as expected to each of the command.

Note: In the MATLAB Command Window, the movement class that appears in real-time during the demonstration simulation, reflects the key currently being depressed (which was assigned during the training process to that movement class):

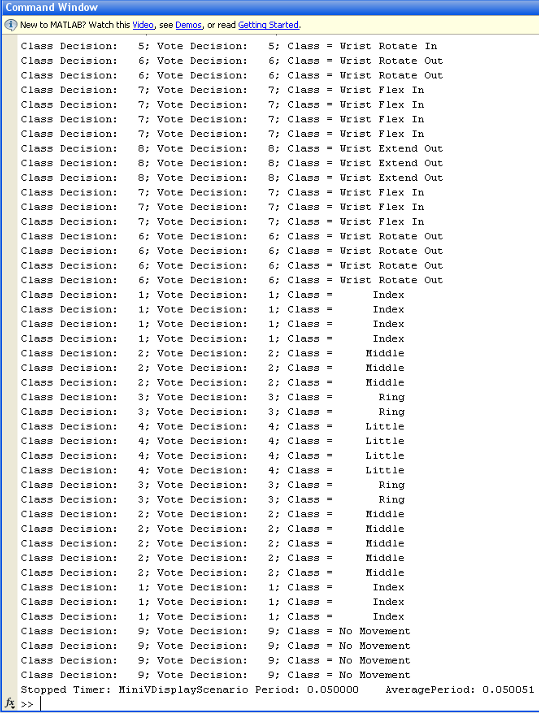
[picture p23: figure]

4. To end the demonstration, exit out of the MiniVIE Display window.

## Appendix A: Setting up Measuring Computing DAQ

Note that this DAQ must be used with MATLAB 32 bit

1. Download the MCC DAQ CD
2. Plug in USB-1208FS
3. Open InstaCal and select configure(hand on circuit board icon)

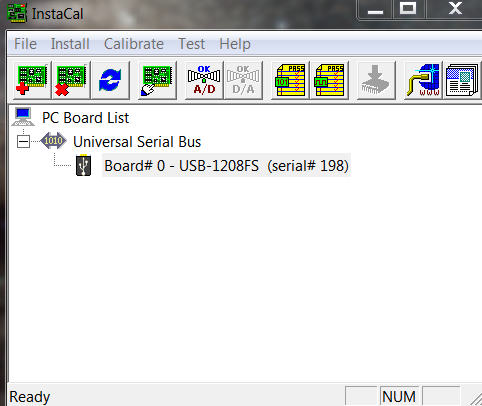
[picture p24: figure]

4. Under No. of Channel, choose 8 Single Ended

## Appendix B: Setting up Limits and Reversing Joints

This section explains how to limit the range of motion for the joints and reverse their direction of motion.

1. In the MiniVIE Configuration Utility window, select the Adjust Limits button.
2. A new window will open showing the current angle limits for each joint

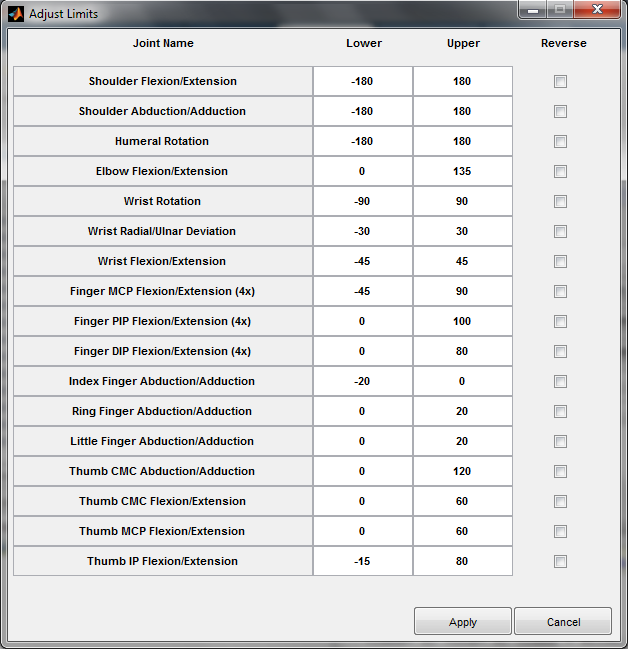
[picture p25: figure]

3. To change a limit, type a new number into the box.
4. If a joint acts in an opposite direction as desired, it can be reversed by checking the Reverse box

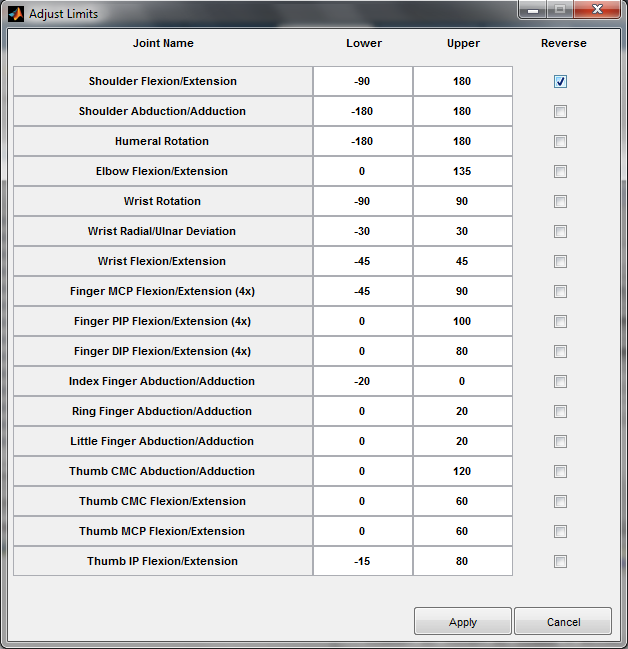
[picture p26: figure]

Note: reversing a joint or changing a limit will not occur until the apply button is selected

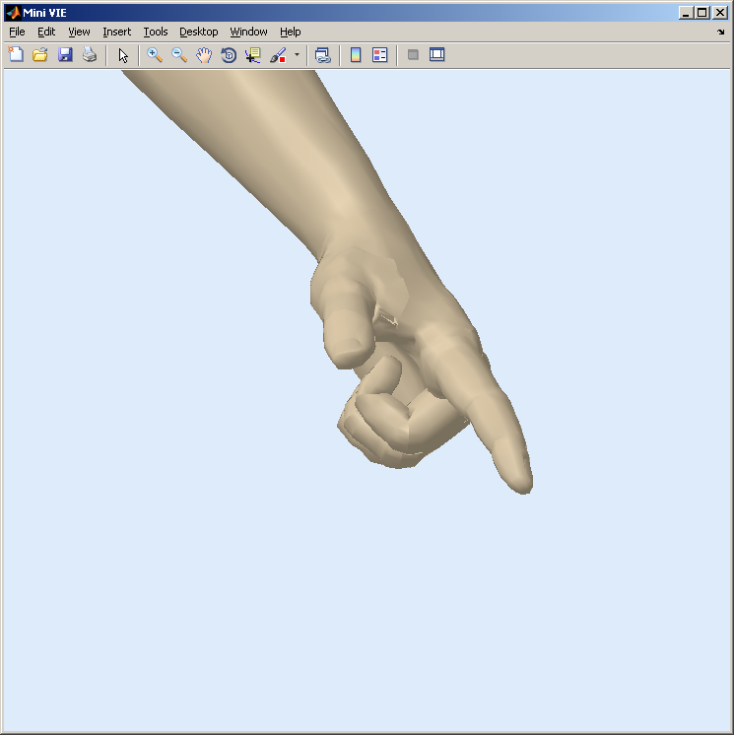
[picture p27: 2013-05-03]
MiniVIE/GUIDE_GUIs/GraspAssistTrainer/Point.TIF

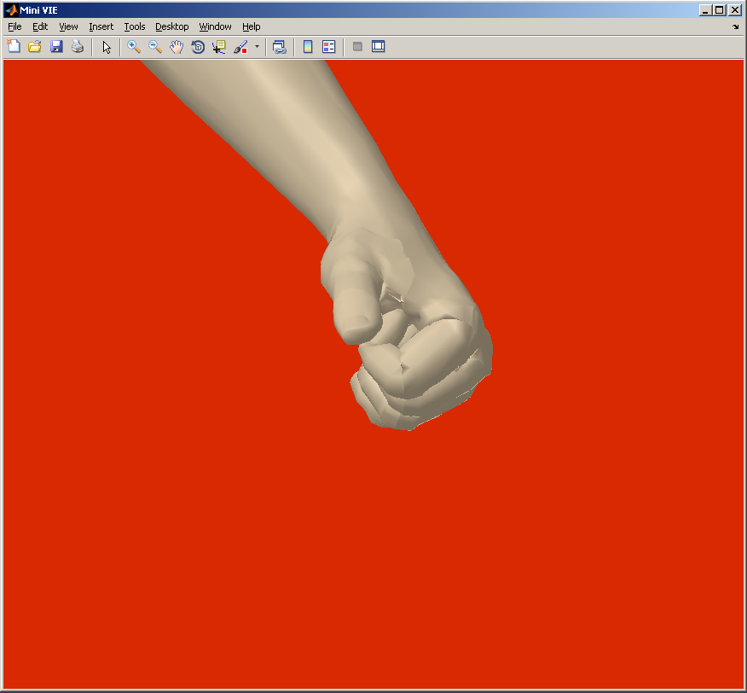
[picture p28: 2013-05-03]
MiniVIE/GUIDE_GUIs/GraspAssistTrainer/Hook_Active.TIF

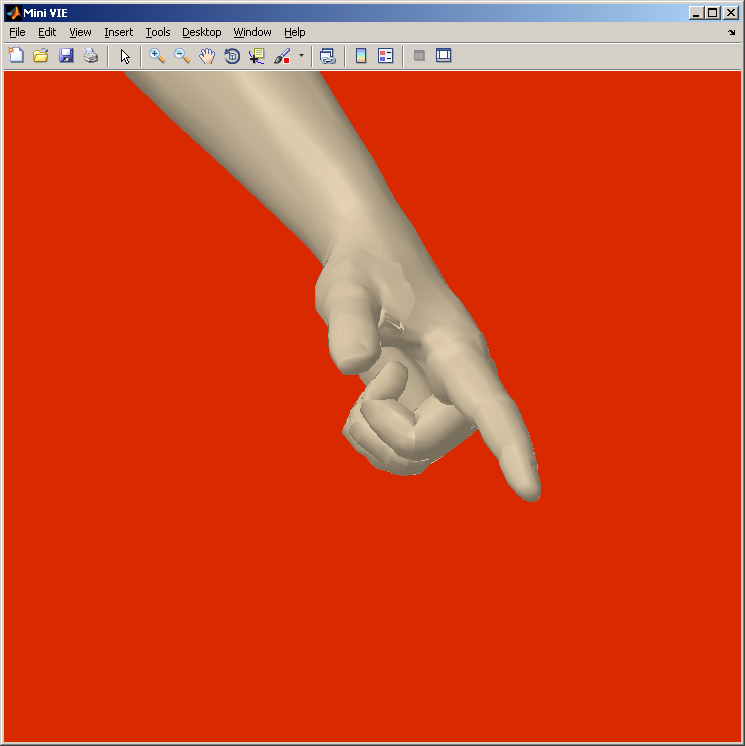
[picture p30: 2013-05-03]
MiniVIE/GUIDE_GUIs/GraspAssistTrainer/Point_Active.TIF

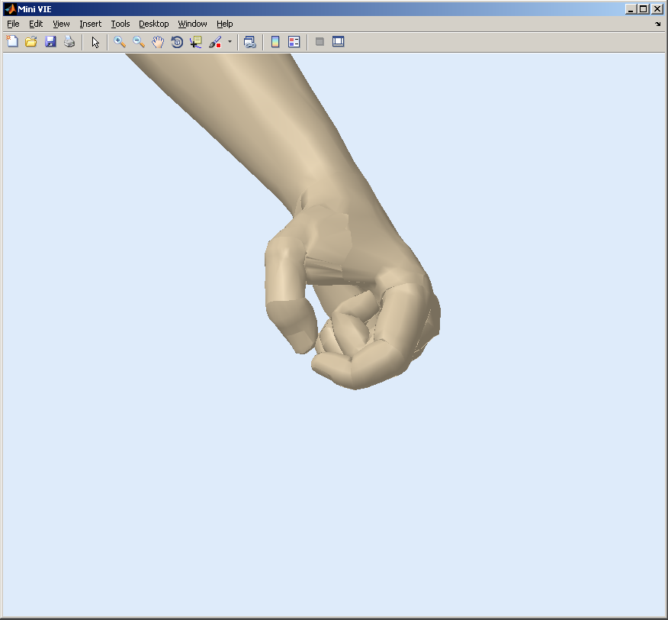
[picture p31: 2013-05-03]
MiniVIE/GUIDE_GUIs/GraspAssistTrainer/CylinderTip.TIF

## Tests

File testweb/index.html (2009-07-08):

# Myopen configuration

Data Stream (port 4340, UDP)

Destination IP:

Cursor control channels:

Mouse x+:
Mouse x-:
Mouse y+:
Mouse y-:

Plot Features:

Feature X:
Channel X:

Feature Y:
Channel Y:

no results yet!

Plot

Feature:
Channel Y:

Binary Conversion

no results still!

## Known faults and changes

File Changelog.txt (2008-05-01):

-----------------------------------
05-01-2008  Tim Hanson sideskate@gmail.com
* Initial import (and open-sourcing) of the emg-dsp design. 
* design is mostly done, just needs some (a lot!) of checking. 
* need to reflow the zones, test DRC.  kicadocaml came up with a few 
	 bits of wire that were not connected (net 0), need to remove. 
* need to add the annotation text to the gerber files to describe how it should
	be manufactured. 
** need to generate & check the drill files, esp. given the two different via sizes. 
* decided to keep the hardware designs in a seperate folder, as I imagine we'll 
	have some software to run on the thing in short time :)
* more later ...

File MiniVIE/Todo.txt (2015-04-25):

To do:

- handle case where new classes are added to existing training data
   - use enums to identify classes
   - verify confusion matrix updated properly

- allow save joint limits
- allow update of active channels
- remove active channels from temp file for bimanual

% Training data management

Within MiniVIE
Training Data is conditionally initialized when classifier selected (if isempty)
(Load function not available until classifier selected)
i.e. training data not reset on classifier change

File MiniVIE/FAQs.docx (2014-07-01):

FAQs Working w/ MiniVIE Code

I changed folders so that my current folder is C:/svn/myopen/MiniVIE, but I am getting the this error message. What am I doing wrong?

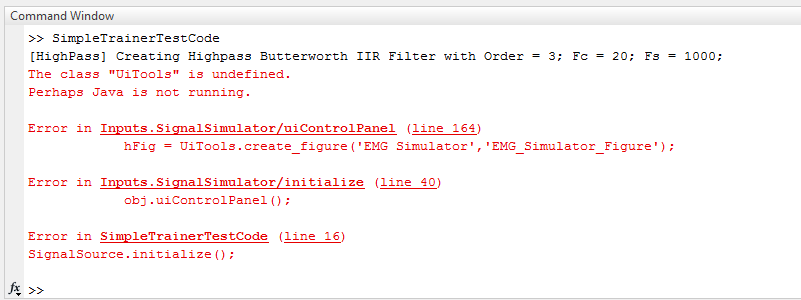
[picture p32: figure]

The key error in this message is the circled line. This lets you know that even though you might be under the MiniVIE directory, you are not connected with the Utilities folder. The Utilities folder contains tools that you need to run your software and must be accessible in order for your program to run. If you are receiving that error Shortcuts message it is because your Current Folder box looks like the image on the left. Go to Shortcuts and click on goto MiniVIE. This is will access the Utilities folder so that your Current Folder looks like the correct image on the right.

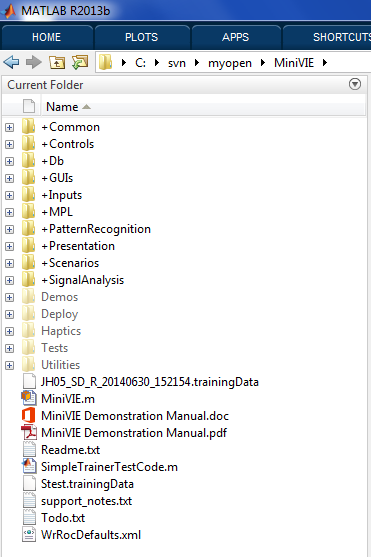
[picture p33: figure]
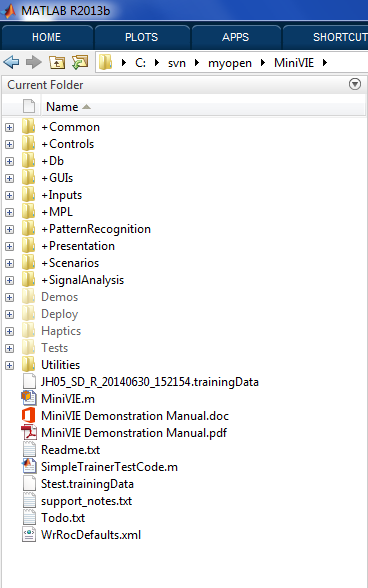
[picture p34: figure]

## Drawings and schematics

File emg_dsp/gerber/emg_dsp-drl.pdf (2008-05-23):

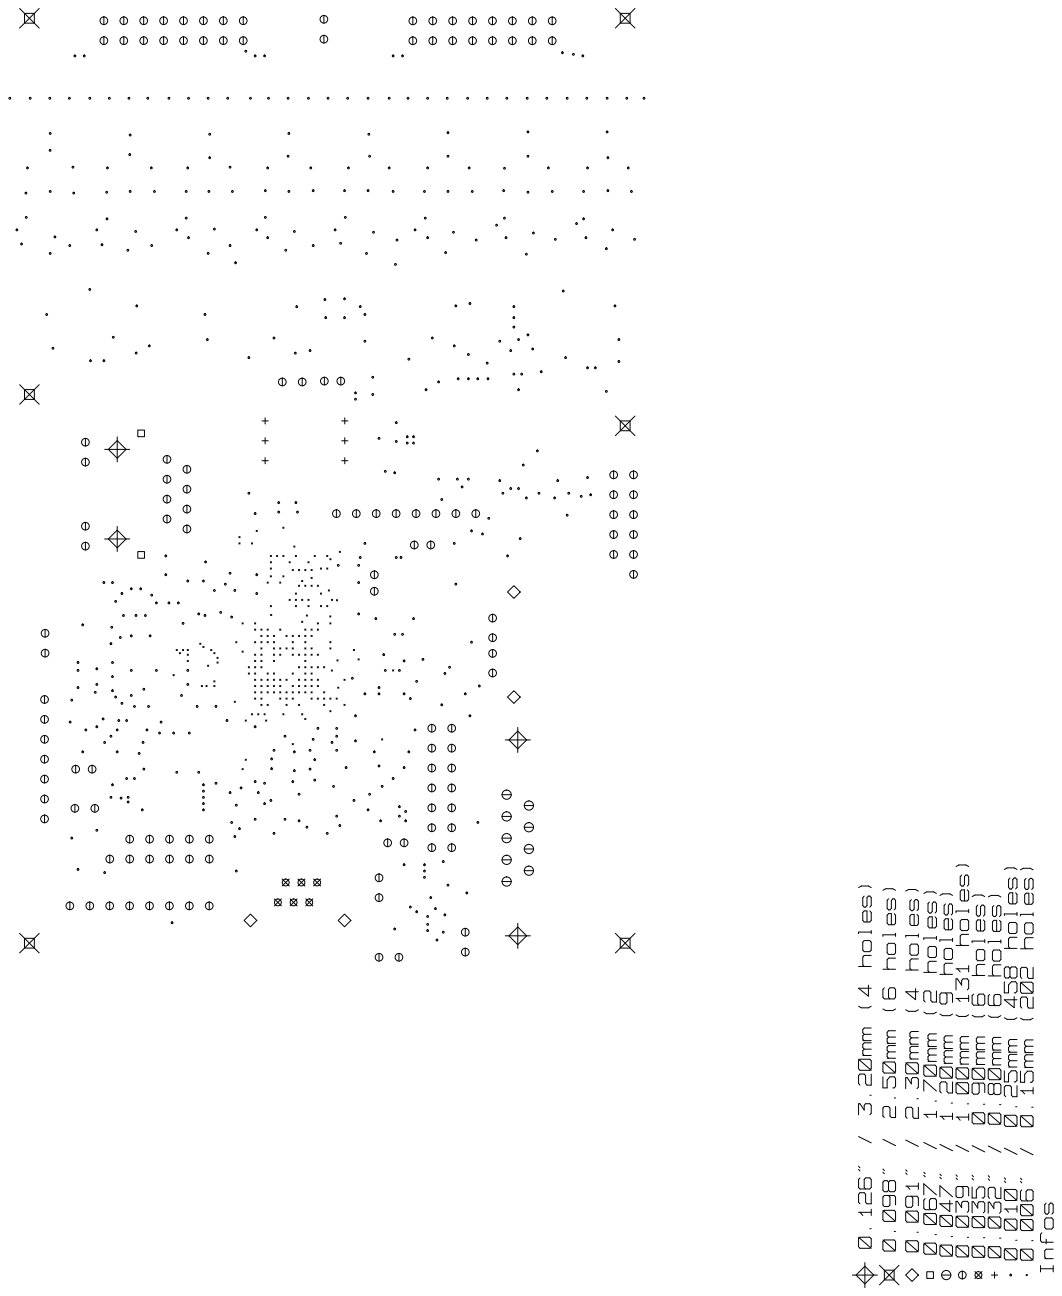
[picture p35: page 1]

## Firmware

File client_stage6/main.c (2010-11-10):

#include <stdio.h>
#include <sys/types.h>
#include <pthread.h>
#include <sys/socket.h>
#include <netinet/in.h>

#include <stdio.h>
#include <stdlib.h>
#include <stdarg.h>
#include <string.h>
#include <GL/glx.h>
#include <GL/gl.h>
#include <GL/glu.h>
#include <X11/keysym.h>
#include <memory.h>
#include <math.h>
#include <arpa/inet.h>

#define NPACKETS 32

typedef struct {
	char data[27]; 
	unsigned char flag; 
	unsigned int exceeded; 
} packet; 
int g_sock = 0;
struct sockaddr_in g_sockAddr; 

static float	g_fbuf[27*NPACKETS*3];
static float 	g_fbufColor[27*NPACKETS*4]; //did the headstage indicate that passed thresh?
unsigned int* g_bufpos;
unsigned int g_sendW; //where to write to (in 32-byte increments)
unsigned int g_sendR; //where to read from
unsigned int g_sendL; //the length of the buffer.

pthread_cond_t 	g_outthread_cond ; 
pthread_mutex_t	g_outthread_mutex ; 
int g_transferred = 0; 
int g_die = 0; 
int g_pause = 0; 
int g_print = 0; 
int g_discont = 0;
float g_zoom = 1.09f; 
float g_offset = 0.f; 
GLuint base;    /* base display list of our font set */
int g_channel = 0; 
int g_headch = 0; 
unsigned int g_exceeded = 0; 
unsigned char g_prev = 0; 
float lowpass_coefs[8] = {0.078146,0.156309,1.261974,-0.614587,
								0.078146,0.156275,0.991706,-0.268803};
float highpass_coefs[8] = {0.983715,-1.967430,1.980324,-0.980949,
								0.983715,-1.967430,1.954002,-0.954619};

float g_gains[32]; //per-channel gains.


/* stuff about our window grouped together */
typedef struct {
    Display *dpy;
    int screen;
    Window win;
    GLXContext ctx;
    XSetWindowAttributes attr;
    int x, y;
    unsigned int width, height;
    unsigned int depth;    
} GLWindow;

/* attributes for a single buffered visual in RGBA format with at least
 * 4 bits per color and a 16 bit depth buffer */
static int attrListSgl[] = {GLX_RGBA, GLX_RED_SIZE, 4, 
    GLX_GREEN_SIZE, 4, 
    GLX_BLUE_SIZE, 4, 
    GLX_DEPTH_SIZE, 16,
    None};

/* attributes for a double buffered visual in RGBA format with at least
 * 4 bits per color and a 16 bit depth buffer */
static int attrListDbl[] = { GLX_RGBA, GLX_DOUBLEBUFFER, 
    GLX_RED_SIZE, 4, 
    GLX_GREEN_SIZE, 4, 
    GLX_BLUE_SIZE, 4, 
    GLX_DEPTH_SIZE, 16,
    None };

GLWindow GLWin;

/* function called when our window is resized (should only happen in window mode) */
void resizeGLScene(unsigned int width, unsigned int height)
{
    if (height == 0)    /* Prevent A Divide By Zero If The Window Is Too Small */
        height = 1;
    glViewport(0, 0, width, height);    /* Reset The Current Viewport And Perspective Transformation */
    glMatrixMode(GL_PROJECTION);
    glLoadIdentity();
    gluPerspective(45.0f, 1 /*(GLfloat)width / (GLfloat)height*/, 0.1f, 100.0f);
    glMatrixMode(GL_MODELVIEW);
}

GLvoid buildFont(GLvoid)
{
    XFontStruct *font;
    
    base = glGenLists(96);      /* storage for 96 characters */
    /* load a font with a specific name in "Host Portable Character Encoding" */
    font = XLoadQueryFont(GLWin.dpy,
        "-*-freesans-bold-r-normal--14-*-*-*-p-*-iso8859-1");
    if (font == NULL)
    {
        /* this really *should* be available on every X Window System...*/
        font = XLoadQueryFont(GLWin.dpy, "fixed");
        if (font == NULL)
        {
            printf("Problems loading fonts :-(\n");
            exit(1);
        }
    }
    /* build 96 display lists out of our font starting at char 32 */
    glXUseXFont(font->fid, 32, 96, base);
    /* free our XFontStruct since we have our display lists */
    XFreeFont(GLWin.dpy, font);
}

GLvoid deleteFont(GLvoid)
{
    glDeleteLists(base, 96);
}

GLvoid printGLf(const char *fmt, ...)
{
    va_list ap;     /* our argument pointer */
    char text[256];
    if (fmt == NULL)    /* if there is no string to draw do nothing */
        return;
    va_start(ap, fmt);  /* make ap point to first unnamed arg */
    /* FIXME: we *should* do boundschecking or something to prevent buffer
     * overflows/segmentations faults
     */
    vsprintf(text, fmt, ap);
    va_end(ap);
    glPushAttrib(GL_LIST_BIT);
    glListBase(base - 32);
    glCallLists(strlen(text), GL_UNSIGNED_BYTE, text);
    glPopAttrib();
}
/* general OpenGL initialization function */
int initGL(GLvoid)
{
    glShadeModel(GL_SMOOTH);
    glClearColor(0.0f, 0.0f, 0.0f, 0.0f);
    glClearDepth(1.0f);
    glEnable(GL_DEPTH_TEST);
    glDepthFunc(GL_LEQUAL);
    glHint(GL_PERSPECTIVE_CORRECTION_HINT, GL_NICEST);
	 glEnable(GL_BLEND); //Enable alpha blending
    glBlendFunc(GL_SRC_ALPHA, GL_ONE_MINUS_SRC_ALPHA); //Set the blend function
	 //glBlendFunc(GL_SRC_ALPHA,GL_ONE);
	 buildFont();        /* create our font-display-lists */
	 //init the vertex buffers
	float* f = g_fbuf; 
	float* t = g_fbufColor; 
	float r,g,b,x,y; 
	r = g = b = 0.6f; 
	for(i=0; i<27*NPACKETS; i++){
		x = (float)i / (float)(27*NPACKETS);
		x = x * 3.f - 1.5f; 
		y = 0.f; 
		*f++ = x; 
		*f++ = y; 
		*f++ = 0.f; 
		*t++ = r;
		*t++ = g; 
		*t++ = b;
		*t++ = 0.4f;
	}
    /* we use resizeGLScene once to set up our initial perspective */
    resizeGLScene(GLWin.width, GLWin.height);
    glFlush();
    return True;
}
/* Here goes our drawing code */
int drawGLScene(GLvoid)
{
	int i, j, len; 
	float x, y, *f; 
	char *c;
	unsigned int off = g_packetOffset; 
	
	glEnableClientState(GL_VERTEX_ARRAY);
	glEnableClientState(GL_COLOR_ARRAY);
	glClear(GL_COLOR_BUFFER_BIT | GL_DEPTH_BUFFER_BIT);
	glLoadIdentity();
	//draw the text before anything else. 
	glTranslatef(0.0f, 0.0f, -1.0f);
	glColor4f(1.f, 1.f, 1.f, 0.6f);
	float offset = 0.f; 
	glRasterPos2f(-0.4f, -0.4f + ((offset+0.f)/(float)GLWin.height));
	printGLf("Present channel - %d (headstage: %d)", g_channel, g_headch);
	glRasterPos2f(-0.4f, -0.4f + ((offset+14.f)/(float)GLWin.height));
	printGLf("thresholds: 0x%x", g_exceeded);
	for(i=31; i>=0; i--){
		glRasterPos2f(-0.4f, -0.4f + ((offset+14.f*(i+2))/(float)GLWin.height));
		printGLf("g[%d] %f",i,g_gains[i]);
	}
	glTranslatef(g_offset, 0.0f, -3.0f);
	glScalef(g_zoom, g_zoom, 1.f); 
	glPointSize(2.0);
	glBegin(GL_LINE_STRIP); 
	glColor4f(1.f, 0.3f, 0.0f, 0.6f);
	float w = 1.5f; 
	float h = 1.f; 
	glVertex3f(-1.f*w, -1.f*h, 0.f); 
	glVertex3f(-1.f*w,  1.f*h, 0.f); 
	glVertex3f( 1.f*w,  1.f*h, 0.f); 
	glVertex3f( 1.f*w, -1.f*h, 0.f); 
	glVertex3f(-1.f*w, -1.f*h, 0.f); 
	glEnd();
	glBegin(GL_LINE_STRIP); 
	glColor4f(1.f, 0.0f, 0.0f, 0.4f);
	glVertex3f(-1.f*w,  0.f*h, 0.f);
	glVertex3f( 1.f*w,  0.f*h, 0.f); 
	glEnd();

	glVertexPointer(3, GL_FLOAT, 0, g_fbuf);
	glColorPointer(4, GL_FLOAT, 0, g_fbufColor);
	glColor4f(1.f, 1.0f, 1.0f, 0.4f);
	glDrawArrays(GL_POINTS, 0, NPACKETS*27);
	glVertexPointer(3, GL_FLOAT, 0, g_fbuf);
	glColorPointer(4, GL_FLOAT, 0, g_fbufColor);
	glColor4f(0.f, 1.0f, 1.0f, 0.4f);
	glDrawArrays(GL_LINE_STRIP, 0, NPACKETS*27);

	glXSwapBuffers(GLWin.dpy, GLWin.win);
	glDisableClientState(GL_VERTEX_ARRAY);
	glDisableClientState(GL_COLOR_ARRAY);

	return True;    
}

/* function to release/destroy our resources and restoring the old desktop */
GLvoid killGLWindow(GLvoid)
{
    if (GLWin.ctx)
    {
        if (!glXMakeCurrent(GLWin.dpy, None, NULL))
        {
            printf("Could not release drawing context.\n");
        }
        glXDestroyContext(GLWin.dpy, GLWin.ctx);
        GLWin.ctx = NULL;
    }
	deleteFont();
	XCloseDisplay(GLWin.dpy);
}

/* this function creates our window and sets it up properly */
/* FIXME: bits is currently unused */
Bool createGLWindow(char* title, int width, int height, int bits,
                    Bool fullscreenflag)
{
    XVisualInfo *vi;
    Colormap cmap;
    int dpyWidth, dpyHeight;
    int i;
    int glxMajorVersion, glxMinorVersion;
    int vidModeMajorVersion, vidModeMinorVersion;
    int modeNum;
    int bestMode;
    Atom wmDelete;
    Window winDummy;
    unsigned int borderDummy;
    
    /* set best mode to current */
    bestMode = 0;
    /* get a connection */
    GLWin.dpy = XOpenDisplay(0);
    GLWin.screen = DefaultScreen(GLWin.dpy);
    /* get an appropriate visual */
    vi = glXChooseVisual(GLWin.dpy, GLWin.screen, attrListDbl);
    if (vi == NULL)
    {
        vi = glXChooseVisual(GLWin.dpy, GLWin.screen, attrListSgl);
        printf("Only Singlebuffered Visual!\n");
    }
    else
    {
        printf("Got Doublebuffered Visual!\n");
    }
    glXQueryVersion(GLWin.dpy, &glxMajorVersion, &glxMinorVersion);
    printf("glX-Version %d.%d\n", glxMajorVersion, glxMinorVersion);
    /* create a GLX context */
    GLWin.ctx = glXCreateContext(GLWin.dpy, vi, 0, GL_TRUE);
    /* create a color map */
    cmap = XCreateColormap(GLWin.dpy, RootWindow(GLWin.dpy, vi->screen),
        vi->visual, AllocNone);
    GLWin.attr.colormap = cmap;
    GLWin.attr.border_pixel = 0;

	/* create a window in window mode*/
	GLWin.attr.event_mask = ExposureMask | KeyPressMask | ButtonPressMask |
		StructureNotifyMask;
	GLWin.win = XCreateWindow(GLWin.dpy, RootWindow(GLWin.dpy, vi->screen),
		0, 0, width, height, 0, vi->depth, InputOutput, vi->visual,
		CWBorderPixel | CWColormap | CWEventMask, &GLWin.attr);
	/* only set window title and handle wm_delete_events if in windowed mode */
	wmDelete = XInternAtom(GLWin.dpy, "WM_DELETE_WINDOW", True);
	XSetWMProtocols(GLWin.dpy, GLWin.win, &wmDelete, 1);
	XSetStandardProperties(GLWin.dpy, GLWin.win, title,
		title, None, NULL, 0, NULL);
	XMapRaised(GLWin.dpy, GLWin.win);     
    /* connect the glx-context to the window */
    glXMakeCurrent(GLWin.dpy, GLWin.win, GLWin.ctx);
    XGetGeometry(GLWin.dpy, GLWin.win, &winDummy, &GLWin.x, &GLWin.y,
        &GLWin.width, &GLWin.height, &borderDummy, &GLWin.depth);
    printf("Depth %d\n", GLWin.depth);
    if (glXIsDirect(GLWin.dpy, GLWin.ctx)) 
        printf("Congrats, you have Direct Rendering!\n");
    else
        printf("Sorry, no Direct Rendering possible!\n");
    initGL();
    return True;    
}

void updateGain(int chan){
	//remember, channels 0 and 16 are written at the same time. 
	//and the biquads are arranged as: 
	// low1 high1 low2 high2
	//olny can adjust the B coefs of the lowpass filters, though.
	//all emitted numbers are base 14.(s2rnd flag)
	chan = chan & 0xf; //map to the lower channels.
	float gain1 = sqrt(g_gains[chan]);
	float gain2 = sqrt(g_gains[chan+16]); 
	int indx [] = {0,1,4,5};
	float b[8]; 
	int i,j,k; 
	unsigned int u; 
	for(i=0; i<4; i++){
		int j = indx[i];
		b[i*2+0] = lowpass_coefs[j]*gain1*16384.f;
		b[i*2+1] = lowpass_coefs[j]*gain2*16384.f;
	}
	//clamp to acceptable values.
	for(i=0; i<8; i++){
		b[i] = b[i] < -32768.f ? -32768.f : b[i];
		b[i] = b[i] > 32767.f ? 32767.f : b[i]; 
	}
	//now form the 32 bit uints to be written. 
	int indx2[] = {0,1,8,9};
	unsigned int* ptr = g_sendbuf; 
	ptr += (g_sendW % g_sendL) * 8; //8 because we send 8 32-bit ints /pkt.
	for(i=0; i<4; i++){
		ptr[i*2+0] = htonl(0xff904000 + chan*16*4 + indx2[i]*4);
		j = (int)(b[i*2+0]);
		k = (int)(b[i*2+1]);
		u = (unsigned int)((j&0xffff) | ((k&0xffff)<<16)); 
		ptr[i*2+1] = htonl(u); 
	}
	g_sendW++; 
}
void setOsc(int chan){
	//turn two channels e.g. 0 and 16 into oscillators.
	float b[4]; 
	unsigned int u; 
	int i,j; 
	b[0] = 0.f; //assume there is already energy in the 
	b[1] = 0.f; //dealy line.
	b[2] = 32768.f - 10; //should be about 250Hz @ fs = 62.5khz
	b[3] = -16384.f; 
	unsigned int* ptr = g_sendbuf; 
	ptr += (g_sendW % g_sendL) * 8; //8 because we send 8 32-bit ints /pkt.
	for(i=0; i<4; i++){
		ptr[i*2+0] = htonl(0xff904000 + (chan*16 + 3*4 + i)*4);
		j = (int)(b[i]);
		u = (unsigned int)((j&0xffff) | ((j&0xffff)<<16)); 
		ptr[i*2+1] = htonl(u); 
	}
	g_sendW++; 
}
void setChan(){
	int i; 
	unsigned int* ptr = g_sendbuf; 
	ptr += (g_sendW % g_sendL) * 8; //8 because we send 8 32-bit ints /pkt.
	ptr[0] = htonl(0xff904500 - 8); //frame pointer
	ptr[1] = htonl(g_channel);
	for(i=2; i<8; i++){
		ptr[i] = 0xa5a5a5a5; 
	}
	g_sendW++; 	
}
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

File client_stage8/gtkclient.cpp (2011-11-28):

// in order to get function prototypes from glext.h, 
// define GL_GLEXT_PROTOTYPES before including glext.h
#define GL_GLEXT_PROTOTYPES

#include <gtk/gtk.h>
#include <gtk/gtkgl.h>
#include <GL/glut.h>    // Header File For The GLUT Library 
#include <GL/gl.h>	// Header File For The OpenGL32 Library
#include <GL/glu.h>	// Header File For The GLu32 Library
#include <GL/glx.h>     // Header file for the glx libraries.
#include "glext.h"
#include "glInfo.h"  

#include <Cg/cg.h>    /* included in Cg toolkit for nvidia */
#include <Cg/cgGL.h>

#include <stdio.h>
#include <sys/types.h>
#include <inttypes.h>
#include <sys/time.h>
#include <pthread.h>
#include <sys/socket.h>
#include <netinet/in.h>
#include <stdlib.h>
#include <stdarg.h>
#include <string.h>
#include <memory.h>
#include <math.h>
#include <arpa/inet.h>
#include "sock.h"

#define NSAMP (24*1024)
#define NDISPW 256
#ifdef EMG
#define NFBUF 8 //for EMG
#else
#define NFBUF 4
#endif

#include "../../neurorecord/stage/memory.h"
#include "headstage.h"
#include "cgVertexShader.h"
#include "vbo.h"
#include "channel.h"
#include "packet.h"
#include <sqlite3.h>
#include "sql.h"
#include <matio.h>
#include <gsl/gsl_math.h>
#include <gsl/gsl_linalg.h>
#include "spikes.pb.h"
#include "tcpsegmenter.h"
#include "firingrate.h"


//CG stuff. for the vertex shaders.
CGcontext   myCgContext;
CGprofile   myCgVertexProfile;
//cgVertexShader*		g_vsFade; 
cgVertexShader*		g_vsFadeColor; 
cgVertexShader*		g_vsThreshold; 

float		g_cursPos[2]; 
float		g_viewportSize[2] = {640, 480}; //width, height.

class Channel; 

static float	g_fbuf[NFBUF][NSAMP*3]; //continuous waveform. range [-1 .. 1]
i64	g_fbufW; //where to write to (always increment) 
i64	g_fbufR; //display thread reads from here - copies to mem
unsigned int 	g_nsamp = 4096; //given the current level of zoom (1 = 4096 samples), how many samples to update?
static float 	g_sbuf[2][128*512*2]; //spike buffers.
static float	g_rasterSpan = 10.f; // %seconds.
i64	g_sbufW[2]; 
i64	g_sbufR[2]; 
Channel*		g_c[128];
FiringRate	g_fr[128][2]; 
GLuint 			base;            // base display list for the font set.

bool g_die = false; 
double g_pause = -1.0;
double g_rasterZoom = 1.0; 
bool g_cycle = false;
bool g_showPca = false; 
bool g_rtMouseBtn = false; 
int g_polyChan = 0; 
bool g_addPoly = false; 
int g_channel[4] = {0,32,64,96}; 
int	g_signalChain = 10; //what to sample in the headstage signal chain.

bool g_out = false; 
bool g_templMatch[128][2]; 
//the headstage match a,b over all 128 channels. cleared after every packet!!
float        g_sortAperture[4][2][16]; //the quality of the match found, circular buffer.
i64			 g_sortOffset[4][2][16]; //offset to the best match.
unsigned int g_sortUnit[4][16]; //have to remember to zero all of these.
unsigned int g_sortI; //index to the (short) circular buffer.
i64			 g_sortWfOffset[4]; 
int 			 g_sortWfUnit[4]; 
i64			 g_unsortCount[4]; 

float g_unsortrate = 10.0; //the rate that unsorted WFs get through.
FILE* g_saveFile = 0; 
bool g_closeSaveFile = false; 
unsigned int g_saveFileBytes;
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

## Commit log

2010-02-17 getting rid of some of the extraneous jumpers... will just have to measure current consumption via the power supply.
    [active_electrode.sch, afe3.sch, amp_0201.sch, microstim.sch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]
2010-02-18 cleaned up the power supplies. not sure what i was thinking before - 2.85V should be fine for Vdd.
    [active_electrode.sch, afe3.sch, amp_0201.sch, microstim.sch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]
2010-02-18 changed the meg isolator to something that will work at 2.7V
    [active_electrode.sch, afe3.sch, amp_0201.sch, microstim.sch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]
2010-02-22 layout 95% done ...
    [active_electrode.sch, afe3.sch, amp_0201.sch, microstim.sch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]
2010-02-23 it's zone time~!
    [active_electrode.sch, afe3.sch, amp_0201.sch, microstim.sch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]
2010-02-23 all pads seem to be connected ... now can do the zones.
    [active_electrode.sch, afe3.sch, amp_0201.sch, microstim.sch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]
2010-02-23 added the zones .. must check them.
    [stage4.brd]
2010-02-25 fixed all but one of the zones ... need to add 'fill selected' zone feature to kicadocaml, as filling all of them takes too long!
    [active_electrode.sch, afe3.sch, amp_0201.sch, microstim.sch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]
2010-02-26 error in teardropping may have left some nets unconnected.
    [stage3.brd]
2010-02-26 fixed some opens resultin from teardropping ..
    [stage4.brd]
2010-02-27 tweaks, removed an unneeded resistor.
    [stage4.brd]
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2010-03-02 added gerber files, added GPL license to the schematics.
    [active_electrode.sch, afe3.sch, amp_0201.sch, microstim.sch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]
2010-03-03 updated the parts list. need to get a few things from Arrow yet, will do that tomorrow.
    [stage4_bom.csv, stage4_bom.ods]
2010-03-24 apparently, I've modified the schematic .. ?
    [active_electrode.sch, afe3.sch, amp_0201.sch, microstim.sch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]
2010-03-24 added notes to the BOM.
    [stage4_bom.csv]
2010-03-31 notes from debugging stage4.
    [active_electrode.sch, afe3.sch, amp_0201.sch, microstim.sch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]
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2010-04-08 commiting changes while actually building be board ..
    [active_electrode.sch, afe3.sch, amp_0201.sch, microstim.sch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]
2010-04-19 new spin of the active elecrode - 0.47" between electrode contacts - two layer design (cheap!!)
    [active_electrode2.brd, active_electrode2.sch]
2010-04-19 I think I'm going to need to array the active electrodes manually - then can put some other stuff on the board too. woohoo.
    [active_electrode2.sch]
2010-05-13 adding the parts list and yushin stored data files.
    [stage4_bom_noEMG.csv, stage4_bottom_part_list.csv, stage4_top_manual_part_list.csv, stage4_top_robot_part_list.csv]
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2010-06-29 working on stage5 !!11!!
    [analog.sch, stage5.sch]
2010-06-30 working on stage5 already -- will it be tight?
    [analog.sch, stage5.brd, stage5.sch]
2010-06-30 routing stage5.
    [analog.sch, stage5.brd, stage5.sch]
2010-07-01 board board bored! need to lay out the other components now.
    [stage5.brd]
2010-07-02 board nearing completion - at least with routing! seems to be a bug in the netlist, though -- have to check it out.
    [analog.sch, stage5.brd, stage5.sch]
2010-07-02 board fully routed - need a few more thermal reliefs. then the zones.
    [analog.sch, stage5.brd, stage5.sch]
2010-07-02 raedy to work on the zones!
    [stage5.brd]
2010-07-02 board loooks good! need to make the gerbers.
    [analog.sch, stage5.brd, stage5.sch]
2010-07-02 okay, this should be a more final version fo the board.
    [stage5.brd]
2010-07-05 sent in the order for all parts & requested a quote for manufacturing the board. hope everything is perfect~!
    [analog.sch, stage5-Back.gbl, stage5-Drawings.gbr, stage5-Front.gtl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]
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2010-09-21 starting another revision -- emg + headstage + bridge.
    [analog.sch, headstage.sch, stage6.sch]
2010-09-22 ethernet, SDRAM, USB connected - not checked of course - but it's a start.
    [analog.sch, emg.sch, neuro.sch]
2010-09-25 need to check all these schematics very carefully - I'm a bit tired tonight! many footprints are not set ...
    [analog.sch, emg_amp.sch, stage6.sch, wired.sch]
2010-09-27 finalizing schematic - next to do: check footprints.
    [analog.sch, emg.sch, emg_amp.sch, neuro.sch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]
2010-09-27 need to make the footprint for the ethernet MAC, then ready to layout ...
    [analog.sch, emg.sch, emg_amp.sch, neuro.sch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]
2010-09-27 time to start laying out the board!
    [analog.sch, emg.sch, emg_amp.sch, neuro.sch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]
2010-09-27 part placement for stage 6 - going to be a moderately large board..
    [active_electrode.sch, afe3.sch, amp_0201.sch, analog.sch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]
2010-09-27 have to lay out the neural headstage .. yet again! this time I'm putting guard rings, though :-)
    [stage6.brd]
2010-09-28 working on the wireless neural part ... low on blood sugar, must go home!
    [analog.sch, emg.sch, emg_amp.sch, neuro.sch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]
2010-09-28 neuro part mostly layed out ...
    [analog.sch, emg.sch, emg_amp.sch, neuro.sch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]
2010-09-28 ethernet partially routed, SDRAM mostly / completely routed. getting there!
    [analog.sch, emg.sch, emg_amp.sch, neuro.sch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]
2010-09-29 wired, wireless, some of bridge are routed. next up is the EMG system.
    [analog.sch, emg.sch, emg_amp.sch, neuro.sch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]
2010-09-29 small mods to be board, checking in before i go home//
    [stage6.brd]
2010-09-30 getting closer -- needt o put DACs on the board so we can listen to the emg / neural data!
    [analog.sch, emg.sch, emg_amp.sch, neuro.sch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]
2010-09-30 added audio out to both the wireless-emg and bridge -- very simple circut, sholud work. layout maybe 70% done.
    [analog.sch, emg.sch, emg_amp.sch, neuro.sch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]
2010-10-01 submitted a (partial) BOM .. !! board is not yet cone, but at least we now know to switch the footprint on the flash.
    [analog.sch, audioout.sch, emg.sch, emg_amp.sch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]
2010-10-05 getting the last of the nets (GND, Vdd, Vcc) routed. still need to check the pinouts, etc.
    [analog.sch, audioout.sch, emg.sch, emg_amp.sch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]
2010-10-06 board getting done! next up is silkscreen - pita.
    [analog.sch, audioout.sch, emg.sch, emg_amp.sch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]
2010-10-06 silkscreen mostly done, the board is very nearly finished!!
    [analog.sch, audioout.sch, emg.sch, emg_amp.sch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]
2010-10-07 board is near-final!!
    [stage6.brd]
2010-10-07 gerbers!!! woo.
    [analog.sch, audioout.sch, emg.sch, emg_amp.sch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]
2010-10-08 still need to check in the gerber changes from home - this checkin is from loco, and concerns the BOMs. recall most of the parts were ordered by Jon.
    [analog.sch, audioout.sch, emg.sch, emg_amp.sch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]
2010-10-08 adding the solder paste masks. these have been submitted to pololu.
    [stage6-SoldP_Back.gbp, stage6-SoldP_Front.gtp]
2010-10-10 fixed some errors in the gerbers.
    [stage6-Back.gbl, stage6-Inner2.gbr, stage6.brd]
2010-10-21 worknig on component placemetn with the robot ..
    [$savepcb.brd, stage6_bom_102010.ods, stage6_bom_robot.csv]
2010-10-26 small mods to the stage6 BOM.
    [stage6_bom_102010.ods]
2010-10-27 forgot about MAX6711T in the robot list.
    [stage6_bom_robot.csv]
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2010-11-10 Initial Revision of the MiniVIE committed added by Bob Armiger, JHU/APL
    [Ball.STL, Table.SLDPRT, Table.STL, Table1.STL]
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2010-12-13 schematic mods... + working on new microstimulator.
    [analog.sch, audioout.sch, emg.sch, emg_amp.sch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]
2010-12-14 woooo working on the next microstimulator.
    [stage7.sch, stim.sch]
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2010-12-22 wireless stimulator!
    [stage7.sch, stim.sch]
2011-01-11 working on 128-channel headstage.
    [analog.sch, audioout.sch, emg.sch, stage8.sch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]
2011-01-12 another damn board! well, at least it's going faster. (not too much changed)
    [analog.sch, stage8.brd, stage8.sch]
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2011-01-21 working on the stimulator - using battery isolation for now. the Burr-brown DC-DC converters tend to generate a bit of noise.
    [audioout.sch, stage7.sch, stim.sch, stim15.sch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]
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2011-01-24 placed modules in stim and wired, issues with shorting in stims
    [audioout.sch, stage7.brd, stage7.sch, stim.sch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]
2011-01-24 finally fixed the VBAT = IGND issue - did so by using wires rather than labels on the inputs to the individual instances of stim.sch yea, that doesn't make sense -should work either way - but ok!
    [audioout.sch, stage7.brd, stage7.sch, stim.sch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]
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2011-02-01 fixed some errors on the board - added a bit to the zone spacing too, 8 mil min clearance, 7 mil min width. (FreeDFM suggested this)
    [stage7.brd, stage7_bom.csv, stage8_bom.csv]
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2011-07-30 mods to the makefile, bugfixes to the python clients.
    [audioout.sch, stage7.sch, stim.sch, stim15.sch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]
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2011-10-26 fixed gerber files. only use kicad for zone fill!!
    [stage10-Back.gbl, stage10-Drawings.gbr, stage10-Front.gtl, stage10-Inner2.gbr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]
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2012-01-11 fixed up the data conversion program. renamed stuff to 'veo' which is a good name ?
    [afe2.sch, afe2_filter.sch, stage2.sch, stage2_amp.sch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]
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2012-04-07 ficed two errors in the board & made two boards!
    [stage10.brd]
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
